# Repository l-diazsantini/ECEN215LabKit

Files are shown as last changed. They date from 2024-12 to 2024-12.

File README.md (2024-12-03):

This is the GitHub repository for Group 30: ECEN 215 Lab Kit from Fall '24, ECEN 404 section 902. This branch contains the firmware code for the final ECEN 215 Lab Kit device. All of the group's reports, presentations, research, meeting notes, etc., can be found in the Documents folder. The PCB and Case folder contains all PCB schematics and case design drawings/markups. All mobile app code can be found in the FlutterFlow branch of this repository.

To operate this device, you must have a physical ECEN 215 Lab Kit and a mobile phone. If using a pre-configured lab kit, the user only needs to press the Enable button through the case to activate the device and connect to it via the mobile application. Please see the FlutterFlow branch for instructions on how to download the application to a mobile device.

If the lab kit is a brand-new PCB, the user will need to connect the Tx, Rx, and GND pins on the PCB to a computer. Once connected, download this code, open it in an Espressif IDF environment, and build and flash the PCB. If done successfully, the Lab Kit will be ready for Bluetooth connection via the mobile application. To operate the lab kit, connect the wires of the corresponding instrument and the device will display the data measured. The wires are given in the order from top row and from left to right:  
<div align="center">
  |  +5v power supply  |  +voltmeter/+oscilloscope  |  ground                    |  +ammeter   |  +ohmmeter |<br>
                                                   |   Wavegen           |  -5v power supply          |  -voltmeter/-oscilloscope  |  -ammeter   |  -ohmmeter  |
</div>
<br>Wires are also color coded in which the wires for +/- power supply are red, +/- voltmeter/oscilloscope are blue, +/- ammeter are orange, +/- ohmmeter are brown, ground is black, and Wavegen is yellow.<br>

The information below provides further insight into how this code enables the onboard ESP32 to connect via Bluetooth.

| Supported Targets | ESP32 | ESP32-C2 | ESP32-C3 | ESP32-C6 | ESP32-H2 | ESP32-S3 |
| ----------------- | ----- | -------- | -------- | -------- | -------- | -------- |

# ESP-IDF Gatt Server Example

This example shows how create a GATT service by adding attributes one by one. However, this method is defined by Bluedroid and is difficult for users to use.

Hence, we also allow users to create a GATT service with an attribute table, which releases the user from adding attributes one by one. And it is recommended for users to use. For more information about this method, please refer to [gatt_server_service_table_demo](../gatt_server_service_table).

This demo creates GATT a service and then starts advertising, waiting to be connected to a GATT client.

To test this demo, we can run the [gatt_client_demo](../gatt_client), which can scan for and connect to this demo automatically. They will start exchanging data once the GATT client has enabled the notification function of the GATT server.

Please, check this [tutorial](tutorial/Gatt_Server_Example_Walkthrough.md) for more information about this example.

## How to Use Example

Before project configuration and build, be sure to set the correct chip target using:

```bash
idf.py set-target <chip_name>
```

### Hardware Required

* A development board with ESP32/ESP32-C3/ESP32-C2/ESP32-H2/ESP-S3 SoC (e.g., ESP32-DevKitC, ESP-WROVER-KIT, etc.)
* A USB cable for Power supply and programming

See [Development Boards](https://www.espressif.com/en/products/devkits) for more information about it.

### Build and Flash

Run `idf.py -p PORT flash monitor` to build, flash and monitor the project.

(To exit the serial monitor, type ``Ctrl-]``.)

See the [Getting Started Guide](https://idf.espressif.com/) for full steps to configure and use ESP-IDF to build projects.

### Settings for UUID128

This example works with UUID16 as default. To change to UUID128, follow this steps:

1. Change the UUID16 to UUID128. You can change the UUID according to your needs.

```c
// Create a new UUID128 (using random values for this example)
uint8_t gatts_service_uuid128_test_X[ESP_UUID_LEN_128] = {0x06, 0x18, 0x7a, 0xec, 0xbe, 0x11, 0x11, 0xea, 0x00, 0x16, 0x02, 0x42, 0x01, 0x13, 0x00, 0x04};
```

By adding this new UUID128, you can remove the `#define` macros with the old UUID16.

2. Add the new UUID128 to the profile.

```c
// Change the size of the UUID from 16 to 128
gl_profile_tab[PROFILE_X_APP_ID].service_id.id.uuid.len = ESP_UUID_LEN_128;
// Copy the new UUID128 to the profile
memcpy(gl_profile_tab[PROFILE_X_APP_ID].service_id.id.uuid.uuid.uuid128, gatts_service_uuid128_test_X, ESP_UUID_LEN_128);
```

3. Remove the following line(s)
```c
gl_profile_tab[PROFILE_X_APP_ID].service_id.id.uuid.uuid.uuid16 = GATTS_SERVICE_UUID_TEST_X;
```

## Example Output

```
I (0) cpu_start: Starting scheduler on APP CPU.
I (512) BTDM_INIT: BT controller compile version [1342a48]
I (522) system_api: Base MAC address is not set
I (522) system_api: read default base MAC address from EFUSE
I (522) phy_init: phy_version 4670,719f9f6,Feb 18 2021,17:07:07
I (922) GATTS_DEMO: REGISTER_APP_EVT, status 0, app_id 0

I (932) GATTS_DEMO: CREATE_SERVICE_EVT, status 0,  service_handle 40

I (942) GATTS_DEMO: REGISTER_APP_EVT, status 0, app_id 1

I (952) GATTS_DEMO: SERVICE_START_EVT, status 0, service_handle 40

I (952) GATTS_DEMO: ADD_CHAR_EVT, status 0,  attr_handle 42, service_handle 40

I (962) GATTS_DEMO: the gatts demo char length = 3

I (962) GATTS_DEMO: prf_char[0] =11

I (972) GATTS_DEMO: prf_char[1] =22

I (972) GATTS_DEMO: prf_char[2] =33

I (982) GATTS_DEMO: CREATE_SERVICE_EVT, status 0,  service_handle 44

I (982) GATTS_DEMO: ADD_DESCR_EVT, status 0, attr_handle 43, service_handle 40

I (992) GATTS_DEMO: SERVICE_START_EVT, status 0, service_handle 44

I (1002) GATTS_DEMO: ADD_CHAR_EVT, status 0,  attr_handle 46, service_handle 44

I (1012) GATTS_DEMO: ADD_DESCR_EVT, status 0, attr_handle 47, service_handle 44

```

## Troubleshooting

For any technical queries, please open an [issue](https://github.com/espressif/esp-idf/issues) on GitHub. We will get back to you soon.

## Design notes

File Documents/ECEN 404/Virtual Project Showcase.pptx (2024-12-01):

## Team 30: ECEN 215 Lab Kit Bi-Weekly Update 5 Members: Luis Diaz-Santini, Yusuf Hossain, Ryan Freed, and Peter Zhang Sponsor: Dr. Lusher TA: Garret Brown

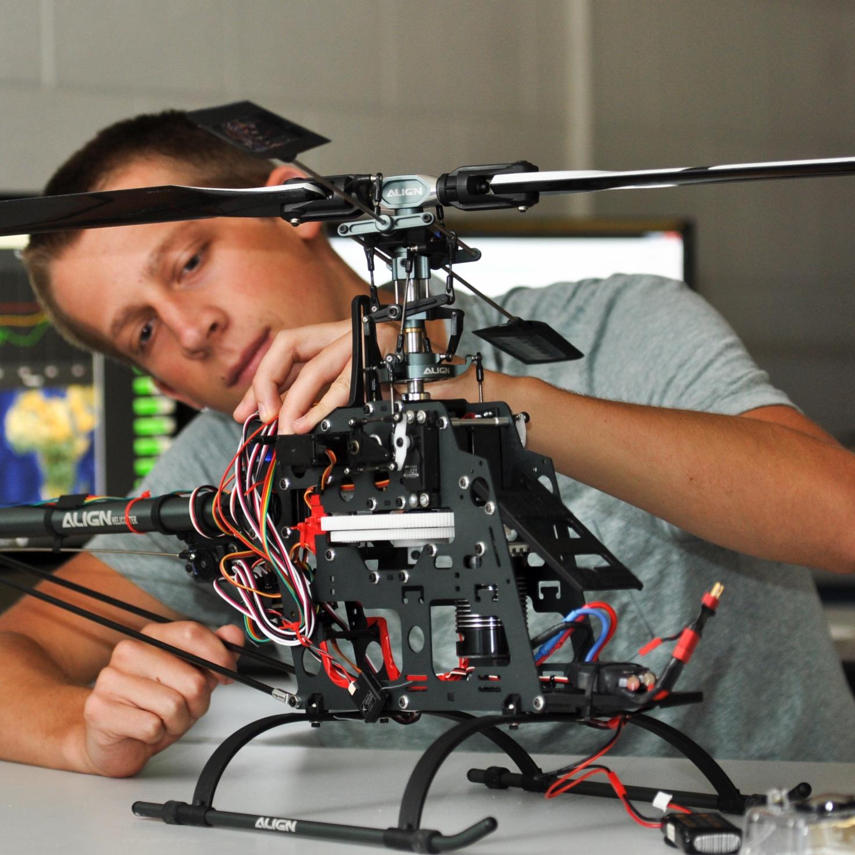
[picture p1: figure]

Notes: Intro should take 30 seconds

## Project Summary

Problem Statement:
- Principles of Electrical Engineering (ECEN 215) teaches the basics of electric circuit analysis and electronics to non-ECEN majors.
- The transition of ECEN 215 to an online format poses a challenge due to its lab component relying on the Analog Discovery 2 (AD2), which is expensive.
Solution Proposal:
- The ECEN 215 Lab Kit offers a solution to the cost, convenience, and over complication issues that are abundant with the AD2. Aiming for a $50 price point, the lab kit offers a more catered simpler approach to each lab while also making it possible to complete at home.
- Will operate as the power supply, signal generator, multimeter, and Oscilloscope.

## Example Lab

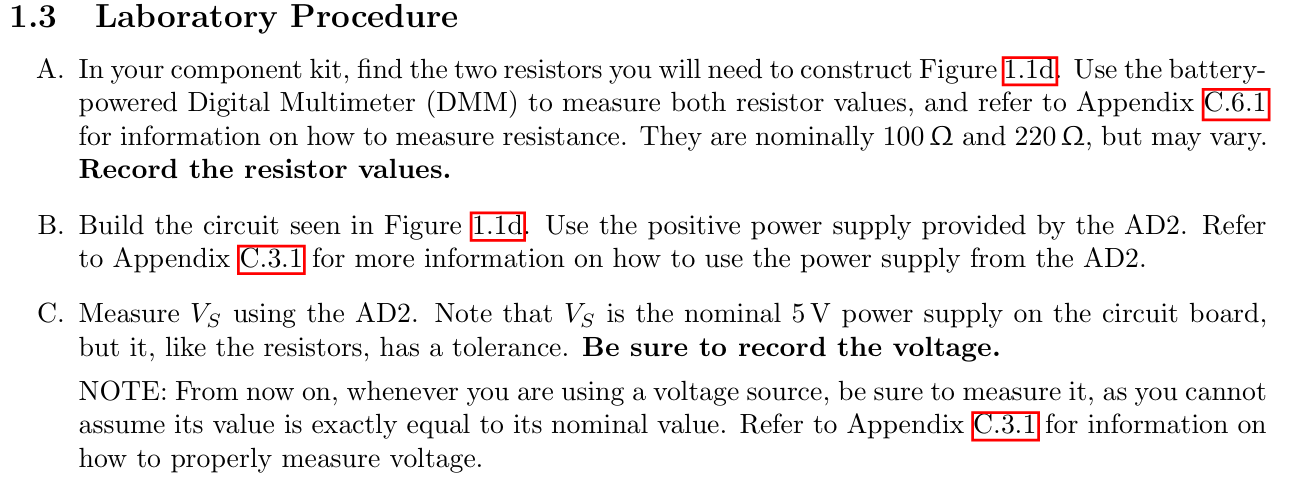
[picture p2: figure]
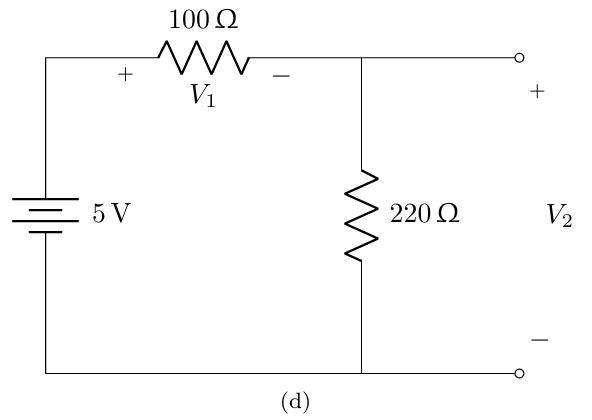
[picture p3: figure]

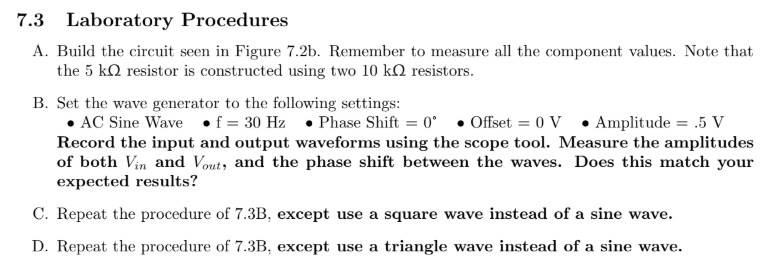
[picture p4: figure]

## Alternatives

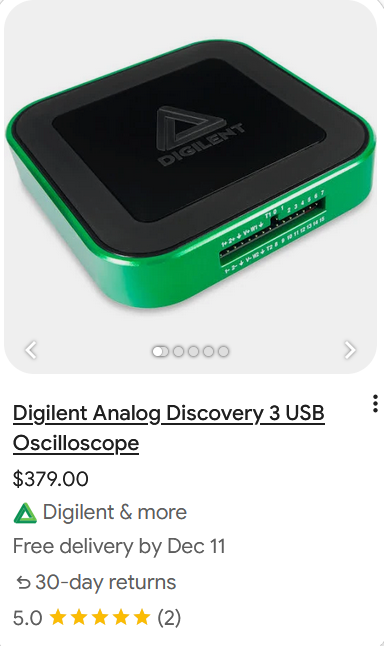
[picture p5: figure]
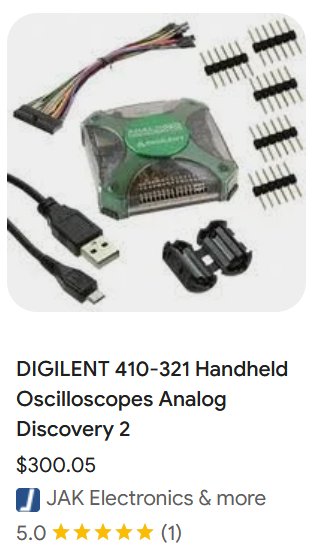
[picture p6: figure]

## Solution Overview

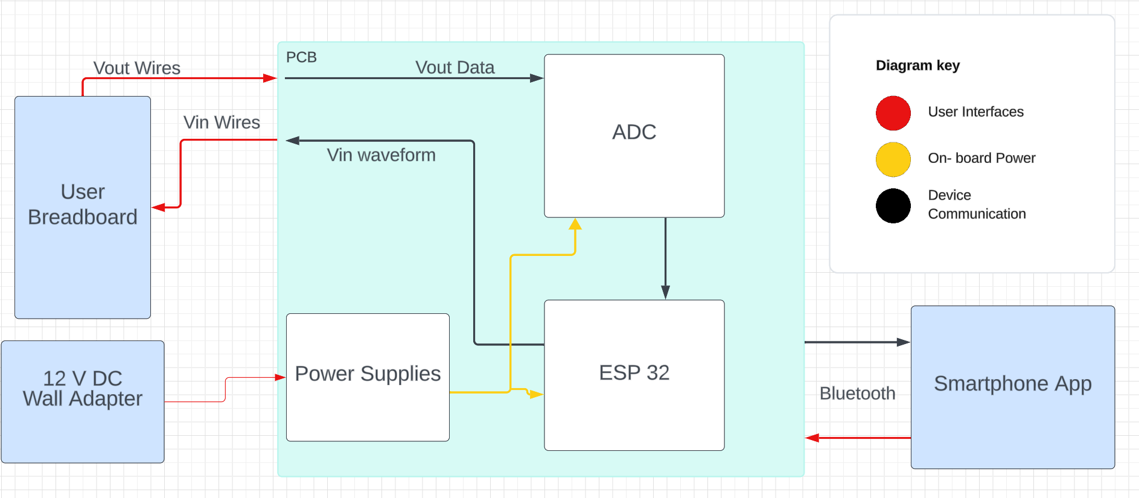
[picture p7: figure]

- Peter: Multimeter and Oscilloscope
- Yusuf: Waveforms and communicating to the microcontroller.
- Luis: Mobile application to interface with device
- Ryan: PCB design and power.

## Oscilloscope and Multimeter Peter Zhang

Accomplishments:
- Design Multimeter (Ammeter, Ohmmeter, Voltmeter)
- Design Oscilloscope
- Read and Modify Data via ESP32
- Transfer Data to App via BLE

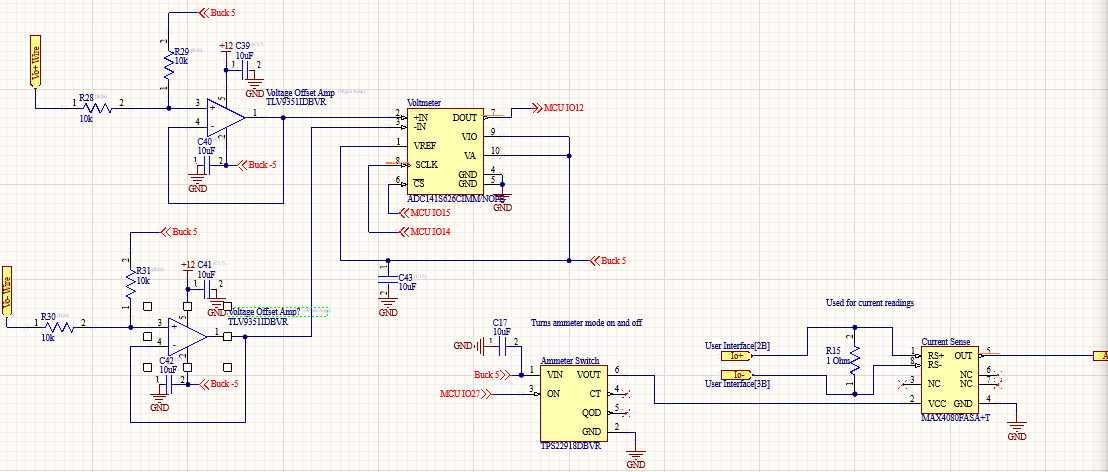
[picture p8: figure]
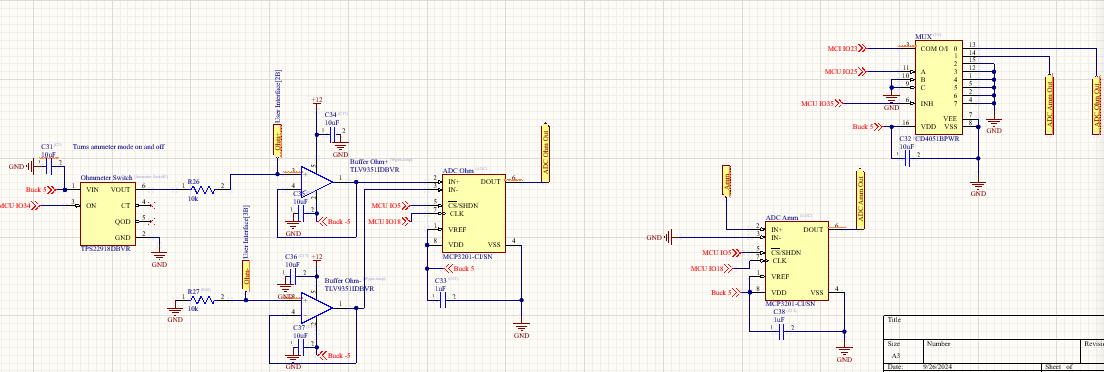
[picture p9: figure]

## Waveform Generator Yusuf Hossain

Validation:

Test | Success Criterion | Results
Wavegen Shapes | Produce Sine, Triangle and square waves
Amplitude | 0.5V, 1V, and 2V
Frequency | 1 Hz, 20 Hz, and 30Hz
Wavegen Noise | Output signal is moderately accurate

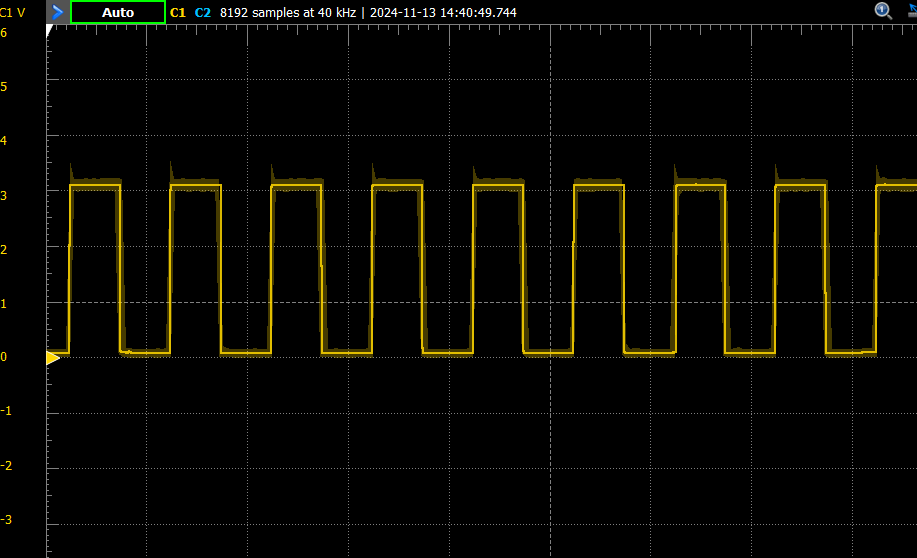
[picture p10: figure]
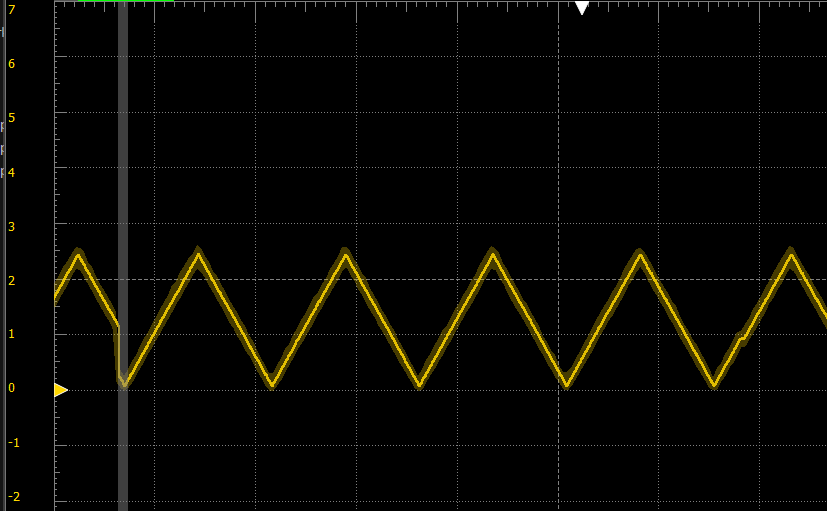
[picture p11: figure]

## Mobile Application

## PCB and Power Ryan Freed

Accomplishments:
- Designed Buck Converters
(5, 3.3, and -5 V)
- Designed Power Supply
switching system (5 and -5 V)
- Designed PCB and case
- Low price and size

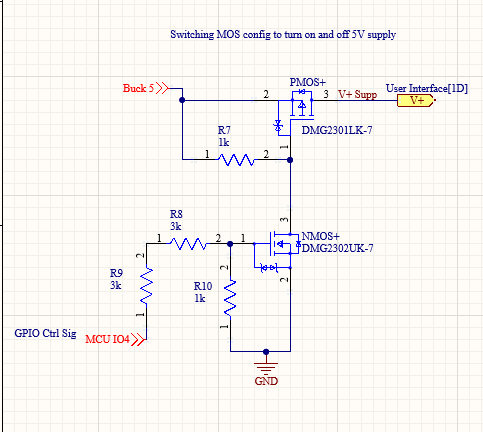
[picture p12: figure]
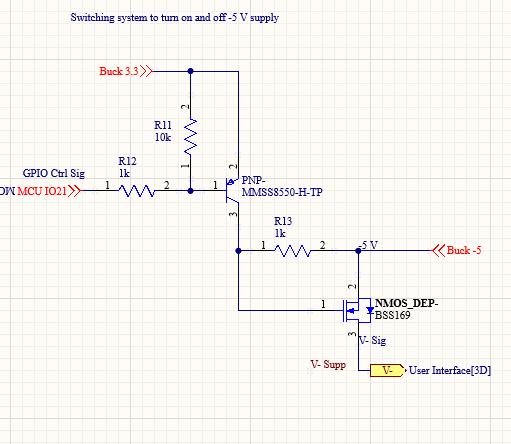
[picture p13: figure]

## Mobile App Validation

- Discovery:
  - Devices are discovered within 4 seconds
- Connection Stability:
  - Verified stable connection to device for at least 30 minutes
- Reconnection:
  - App can disconnect from device and reconnect immediately
- Read/Write Operations:
  - Verified app sending/receiving messages through VSCode terminal and system functionality
- Connection Latency:
  - App constantly connects within 1.5 second
- Command Response Time:
  - Data is sent to the app within 0.25 seconds after requesting
- Device Compatibility:
  - App has been installed and operated on multiple devices with various software anywhere from 2 years of age to 10 years of age
- Interference:
  - In performing this demo the app shows stable connection in an environment with abundant BL traffic

## Multimeter/Oscilloscope Validation

- App-Multimeter Connectivity
  - Microcontroller sends data through bluetooth to the app from terminal and system functionality
- App-Oscilloscope Connectivity:
  - Graphed oscilloscope readings onto app

Voltage
Expected | Actual | Percent Error
5 V | 4.96V | 0.8%
2.5 V | 2.43 | 2.8%
0 V | .024 | ~~~

Resistance
Expected | Actual | Percent Error
10000 | 9814.343 | 1.89%
1000 | 1005.385 | 0.09%
100 | 108.28 | 7.6%

## PCB/Power Validation

Power Systems Results | Expected | Actual
System 1 | 5 V | 4.987
System 2 | 3.3 V | 3.319
System 3 | -5 V | -4.976

Switching System Results | ESP Low | ESP High
Switch 1 | 0.019 mV | 4.93 V
Switch 2 | -4.975 V | -4.973 V

## PCB/Power Validation

Price and Size Analysis:
- Altium Price Analysis: $44.57
- JLC Price Analysis per 500: $3.80
- Wall Adapter: $8.83
- Overall Estimate: $57.20 per board
- Case Size: 156.7x85.6x21.7mm
- Area increase vs. phone: 24%

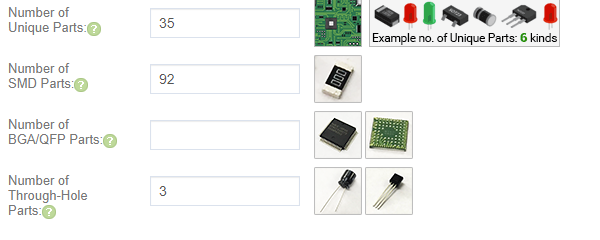
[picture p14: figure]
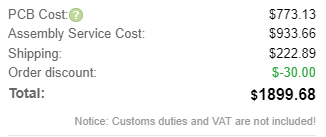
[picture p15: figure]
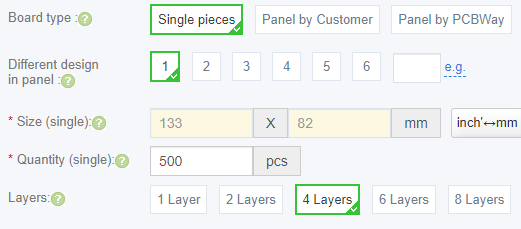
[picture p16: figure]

## ECEN 215 Lab Kit

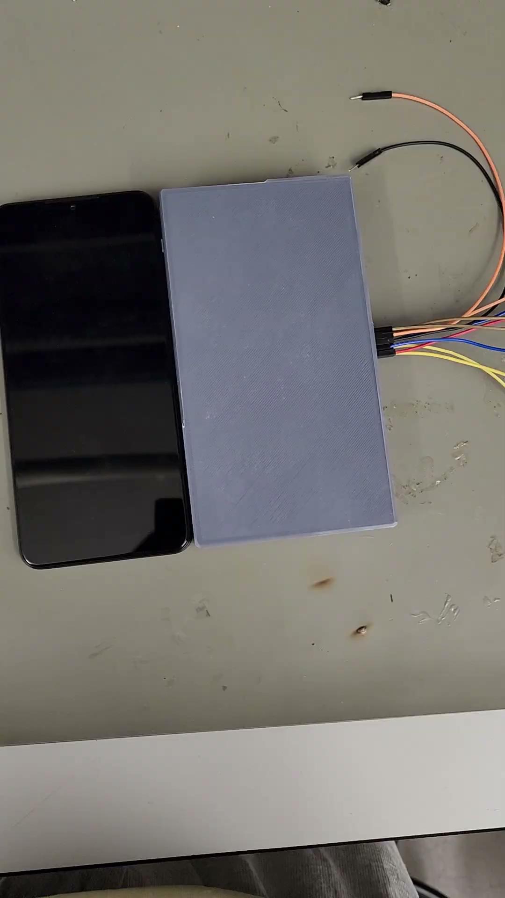
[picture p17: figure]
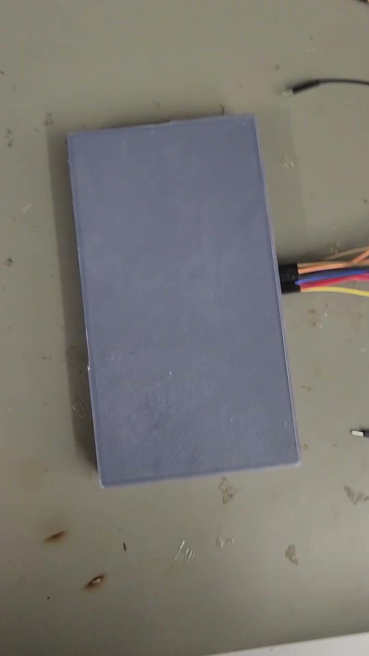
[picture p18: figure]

## Multimeter: Ammeter and Ohmmeter

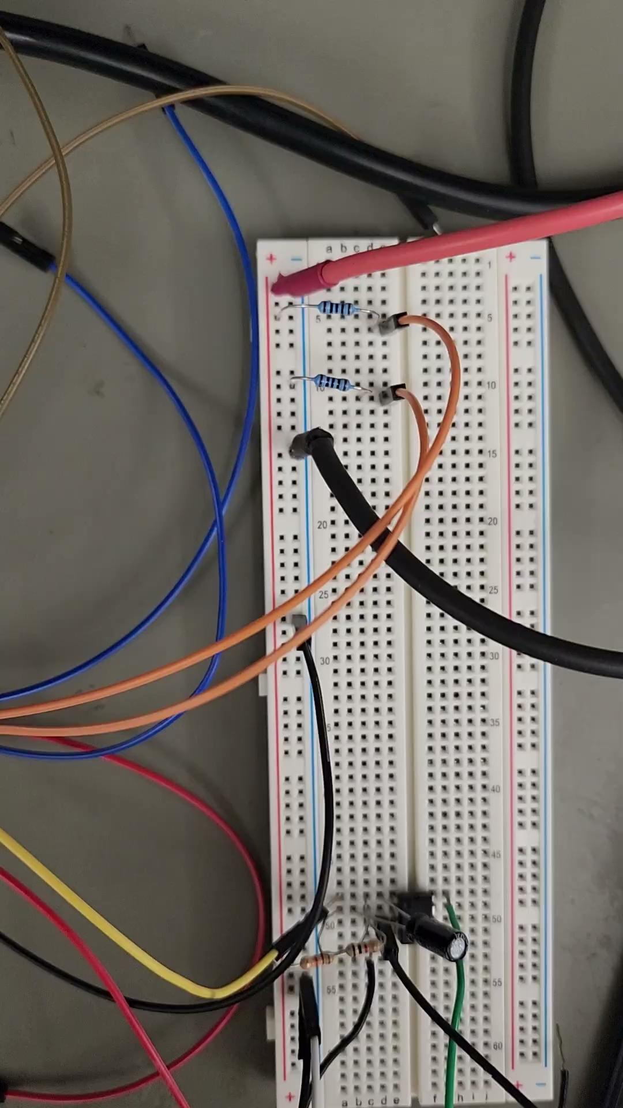
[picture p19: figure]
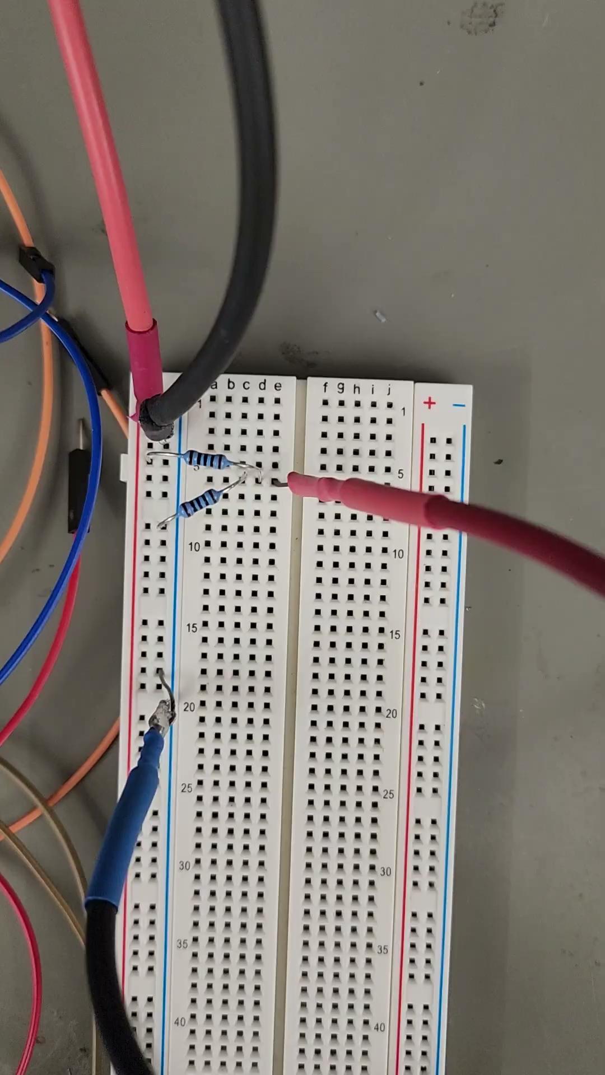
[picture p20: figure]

## Multimeter: Ohmmeter

## Oscilloscope: Sine, Square, and Triangle

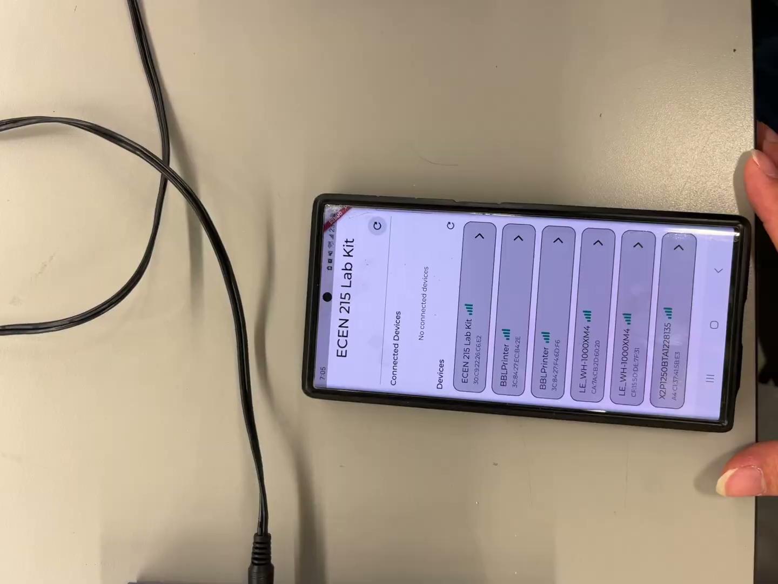
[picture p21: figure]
Sine
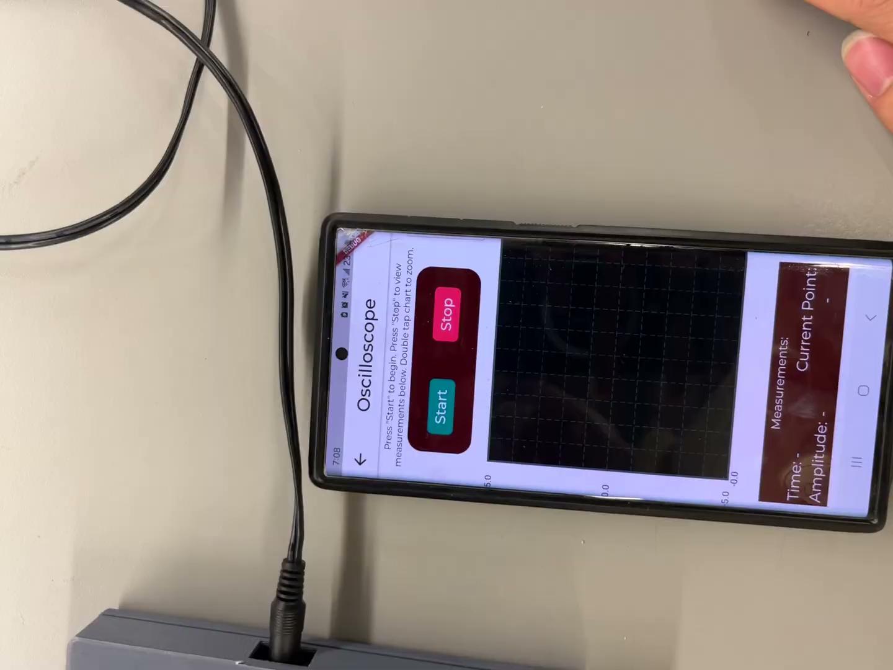
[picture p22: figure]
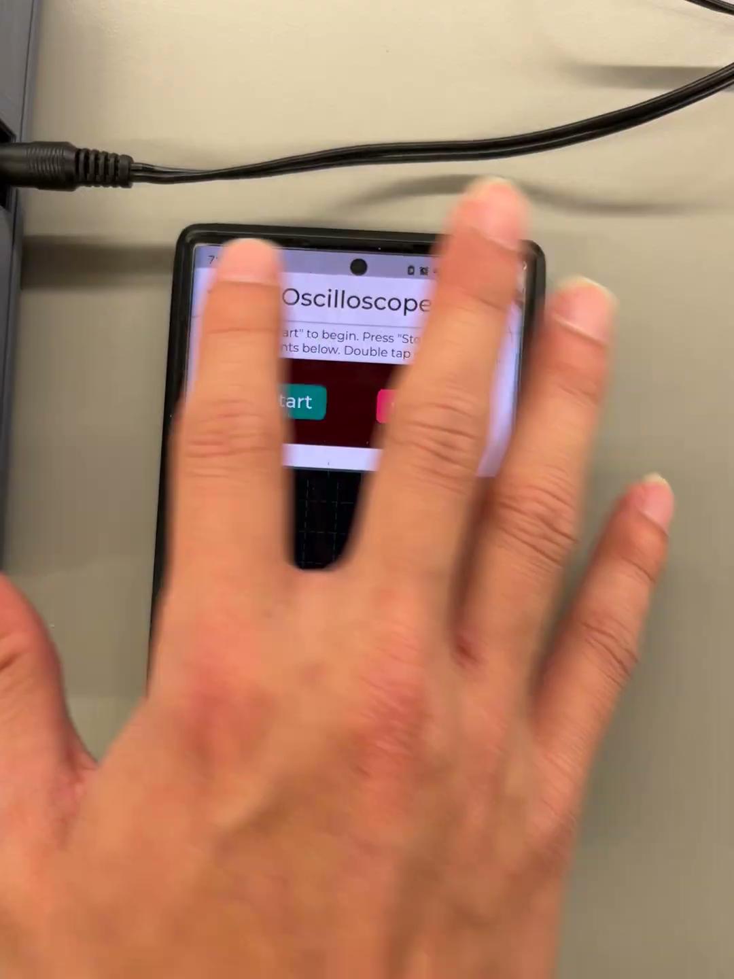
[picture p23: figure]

## Wavegen: Sine, Square, and Triangle

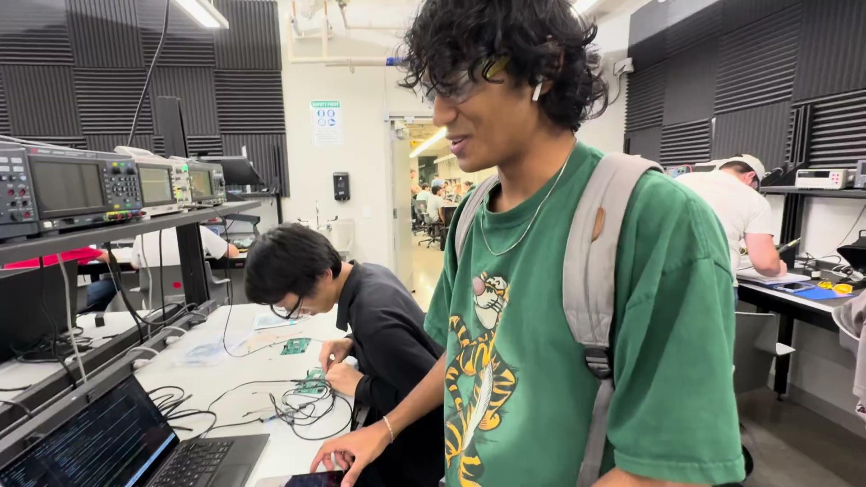
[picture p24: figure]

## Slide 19

Thank you

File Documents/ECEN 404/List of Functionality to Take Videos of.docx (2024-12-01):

Check off what we have recorded:

- Multimeter
  - ~~Voltmeter - measuring 3 different voltages, validate with real multimeter~~
  - Ammeter - measuring 3 different currents, validate with real multimeter
  - ~~Ohmmeter - measuring 3 different resistances, validate with real multimeter~~
- ~~Oscilloscope~~
  - ~~Display constant voltage applied to a system~~
  - ~~Display AC voltages (square, sine, or triangular)~~
  - ~~Show amplitude and time~~
- ~~Waveform Generator (show measurements on an oscilloscope if accurate???)~~
  - ~~Square - all three~~
  - ~~Sine - all three~~
  - ~~Triangular - just the one~~
- Power Supply
  - ~~+5V activation and output~~
  - -5V activation and output

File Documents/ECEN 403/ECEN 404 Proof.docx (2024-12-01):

Peter Zhang


Ryan Freed


Luis Diaz-Santini


Yusuf Hossain


f


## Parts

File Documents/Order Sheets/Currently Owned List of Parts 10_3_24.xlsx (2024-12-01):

Part Name | Disc | Link | Num Parts | I/O (EX: -1) | Date I/O
08055C104JAT4A | 0.1 uF Capacitor | https://www.mouser.com/ProductDetail/KYOCERA-AVX/08055C104JAT4A?qs=xMTsDkQFXIwrNDKsf1C%2F4A%3D%3D | 2
584-AD9833BRMZ | DAC/ADC Special | https://www.mouser.com/ProductDetail/Analog-Devices/AD9833BRMZ?qs=BpaRKvA4VqFt3Bdw9RBKCQ%3D%3D | 1
726-BSS169H6327 | N-Channel Mosfet 2.9 Vgs,th | https://www.mouser.com/ProductDetail/Infineon-Technologies/BSS169-H6327?qs=wsCKvrPXYihFtZGZbPOydw%3D%3D | 2
926-LM2611BMFX/NOPB (https://www.mouser.com/ProductDetail/926-LM2611BMFX-NOPB) | Switching Volt Reg | https://www.mouser.com/ProductDetail/926-LM2611BMFX-NOPB | 1
AC0603FR-0729K4L | 29.4k Resistor | https://www.mouser.com/ProductDetail/YAGEO/AC0603FR-0729K4L?qs=UBLIud9aIG2k8zKS2xVklQ%3D%3D | 7
C0603C331M5HACTU | cer cap | https://www.mouser.com/ProductDetail/KEMET/C0603C331M5HACTU?qs=W0yvOO0ixfErkuKIu%252BxRBQ%3D%3D | 8
C3216X5R1E476M160AC | Cer Cap | https://www.mouser.com/ProductDetail/TDK/C3216X5R1E476M160AC?qs=NRhsANhppD%252BqapdVvBvu4Q%3D%3D | 1
CDBU0130L-HF | Schotty Diode | https://www.mouser.com/ProductDetail/Comchip-Technology/CDBU0130L-HF?qs=2qJf6qQ4IOJ7bRynSa%252B09g%3D%3D | 1
CL21A106KAYNNNF | 10 uF Capacitor | https://www.mouser.com/ProductDetail/Samsung-Electro-Mechanics/CL21A106KAYNNNF?qs=xZ%2FP%252Ba9zWqbNXsT2s0u%252B1w%3D%3D | 1
CRCW060373K2FKEA | Fil Res | https://www.mouser.com/ProductDetail/Vishay-Dale/CRCW060373K2FKEA?qs=wtKLRx7HFiWbNo88VwpoiQ%3D%3D | 8
DMG2301LK-7 | P-Channel MOSFET 0.3 Vgs,th | https://www.mouser.com/ProductDetail/Diodes-Incorporated/DMG2301LK-7?qs=rN85NNvew%2FQ%252B%2FQuwyP8KUg%3D%3D | 1
DMG2302UK-7 | N-Channel MOSFET 0.3 Vgs,th | https://www.mouser.com/ProductDetail/Diodes-Incorporated/DMG2302UK-7?qs=nJRy1mI8RR8oxdwFJAgjOg%3D%3D | 2
LM321LVIDBVR | Op Amp | https://www.mouser.com/ProductDetail/Texas-Instruments/LM321LVIDBVR?qs=qSfuJ%252Bfl%2Fd66sZ569ResAQ%3D%3D | 3
MBR0520-TP | Schotty Diode | https://www.mouser.com/ProductDetail/Micro-Commercial-Components-MCC/MBR0520-TP?qs=Oupk%2FUD005gN%2Fsy5ULAgCw%3D%3D | 3
MBR0580-TP | Schottky Diodes 80V 5.5 A | https://www.mouser.com/ProductDetail/Micro-Commercial-Components-MCC/MBR0580-TP?qs=O1HRStiETCj2wMrWH4Z8DQ%3D%3D | 2
MMSS8550-H-TP | PNP BJT | https://www.mouser.com/ProductDetail/Micro-Commercial-Components-MCC/MMSS8550-H-TP | 2
NR8040T4R7N | 4.7 uH Induct | https://www.mouser.com/ProductDetail/TAIYO-YUDEN/NR8040T4R7N?qs=PzICbMaShUcp7zkwLhhm8A%3D%3D | 1
RK73H1JTTDD1002F | 10K Res | https://www.mouser.com/ProductDetail/KOA-Speer/RK73H1JTTDD1002F?qs=b1MjUb3%252BcaU0rYKbWd%2FWJg%3D%3D | 3
RMCF1210FT1R00 | 1 ohm Res | https://www.mouser.com/ProductDetail/SEI-Stackpole/RMCF1210FT1R00?qs=IPgv5n7u5QY%252BgVPKo7K9fw%3D%3D | 8
RT0603FRE0745K3L | Fil Res | https://www.mouser.com/ProductDetail/YAGEO/RT0603FRE0745K3L?qs=4CyHz7GXqSjZdK2aq1DdCA%3D%3D | 8
SRP1265WA-470M | Pow Induct | https://www.mouser.com/ProductDetail/Bourns/SRP1265A-470M?qs=7z%252BmIopC6%2FJVBbWifq3cvA%3D%3D | 1
SRR1260-150M | Pow Induct | https://www.mouser.com/ProductDetail/Bourns/SRR1260-150M?qs=y9m3SKnhpLPF5BoYDkDwgQ%3D%3D | 2
TPS22918DBVR | Power Switch | https://www.mouser.com/ProductDetail/Texas-Instruments/TPS22918DBVR?qs=f4l5qYp%2Fy%252B5F7w5ZAgmi7A%3D%3D | 1
TPS629203QDRLRQ1 (https://www.mouser.com/ProductDetail/595-TPS629203QDRLRQ1) | Switching voltage regulator 3V to 17V | https://www.mouser.com/ProductDetail/595-TPS629203QDRLRQ1 | 5
CL21A226MAYNNNE | 22 uF Capacitor | https://www.mouser.com/ProductDetail/Samsung-Electro-Mechanics/CL21A226MAYNNNE?qs=xZ%2FP%252Ba9zWqY%2FVvCfXjMhqg%3D%3D | 6
710-694108105102 | Horizontal Wall Wort | https://www.mouser.com/ProductDetail/Wurth-Elektronik/694108105102?qs=a9WhcLg8qCxZ8uWYc7A1TQ%3D%3D | 1
EVQQ1D06M | Button | https://www.mouser.com/ProductDetail/Panasonic/EVQ-Q1D06M?qs=aeOb9a4xWfmdGmKk3ZcvYg%3D%3D | 2
EVP-AKE31A | Button | https://www.mouser.com/ProductDetail/Panasonic/EVP-AKE31A?qs=EU6FO9ffTwe%252BJzX5LvvHqA%3D%3D | 3
PREC003SAAN-RC | Male-Male Vertical header | https://www.digikey.com/en/products/detail/sullins-connector-solutions/PREC003SAAN-RC/2774851?s=N4IgTCBcDaIAoCUCiBhADGgzAZQIK4DkBaBFEAXQF8g | 9
CL10A105KA8NNND | 1 uF Cap | https://www.mouser.com/ProductDetail/Samsung-Electro-Mechanics/CL10A105KA8NNND?qs=xZ%2FP%252Ba9zWqZr4yEmwBAKRg%3D%3D | 7
CR0805-FX-3001ELF | 3k Res | https://www.mouser.com/ProductDetail/Bourns/CR0805-FX-3001ELF?qs=4vGXhLEMbUyE0MonUw6pjA%3D%3D | 5
356-ESP32C6WROOM1N8 (https://www.mouser.com/ProductDetail/356-ESP32C6WROOM1N8) | ESP32-C6-WROOM-1-N8 (https://www.mouser.com/ProductDetail/356-ESP32C6WROOM1N8) | https://www.mouser.com/ProductDetail/356-ESP32C6WROOM1N8

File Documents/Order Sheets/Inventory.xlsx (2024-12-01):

Part name | Desc | Link | Current Inventory | Required Inventory |  | Minimum needed | If neg don't need it | Buck Needs
694108105102 | Power Jack | https://www.mouser.com/ProductDetail/Wurth-Elektronik/694108105102?qs=a9WhcLg8qCxZ8uWYc7A1TQ%3D%3D | 1 | 1 |  | 0
08055C104JAT4A | 0.1 uF 50VDC | https://www.mouser.com/ProductDetail/KYOCERA-AVX/08055C104JAT4A?qs=xMTsDkQFXIwrNDKsf1C%2F4A%3D%3D | 22 | 16 |  | -6 |  | 8 | *
AC0603FR-0729K4L | 29.4k 100mW | https://www.mouser.com/ProductDetail/YAGEO/AC0603FR-0729K4L?qs=UBLIud9aIG2k8zKS2xVklQ%3D%3D | 7 | 1 |  | -6
ADC141S626CIMM/NOPB | ADC 14 bit | https://www.mouser.com/ProductDetail/Texas-Instruments/ADC141S626CIMM-NOPB?qs=7X5t%252BdzoRHCk2zqpP70%252BpA%3D%3D | 1 | 1 |  | 0
BSS169 | NMOS 100V 90mA | https://www.mouser.com/ProductDetail/Infineon-Technologies/BSS169H6327XT?qs=Pidqk4Lw9ynD4CFbvj57WQ%3D%3D | 2 | 1 |  | -1
C0603C331M5HACTU | 333pF 50VDC | https://www.mouser.com/ProductDetail/KEMET/C0603C331M5HACTU?qs=W0yvOO0ixfErkuKIu%252BxRBQ%3D%3D | 8 | 1 |  | -7
C3216X5R1E476M160AC |  | https://www.mouser.com/ProductDetail/TDK/C3216X5R1E476M160AC?qs=NRhsANhppD%252BqapdVvBvu4Q%3D%3D | 1 | 2 | Replaced by MLASE31LBB5476MTNA01 | 1 |  | 2
CD4051BPWR | 8 channel mux | https://www.mouser.com/ProductDetail/Texas-Instruments/CD4051BPWR?qs=dQbkqP7qjabkyiIdB0m30Q%3D%3D |  | 1 |  | 1
CL10A105KA8NNND | 1uF 25VDC | https://www.mouser.com/ProductDetail/Samsung-Electro-Mechanics/CL10A105KA8NNND?qs=xZ%2FP%252Ba9zWqZr4yEmwBAKRg%3D%3D | 7 | 3 |  | -4
CL21A106KAYNNNF | 10uF 25VDC | https://www.mouser.com/ProductDetail/Samsung-Electro-Mechanics/CL21A106KAYNNNF?qs=xZ%2FP%252Ba9zWqbNXsT2s0u%252B1w%3D%3D | 11 | 14 |  | 3 |  | 2 | *
CL21A226MAYNNNE | 22uF 25VDC | https://www.mouser.com/ProductDetail/Samsung-Electro-Mechanics/CL21A226MAYNNNE?qs=xZ%2FP%252Ba9zWqY%2FVvCfXjMhqg%3D%3D | 6 | 2 |  | -4
CR0805-FX-3001ELF | 3k 125mW | https://www.mouser.com/ProductDetail/Bourns/CR0805-FX-3001ELF?qs=4vGXhLEMbUyE0MonUw6pjA%3D%3D | 5 | 2 |  | -3
CRCW060373K2FKEA | 73.2k 100mW | https://www.mouser.com/ProductDetail/Vishay-Dale/CRCW060373K2FKEA?qs=wtKLRx7HFiWbNo88VwpoiQ%3D%3D | 8 | 1 |  | -7
DMG2301LK-7 | PMOS 20VDS | https://www.mouser.com/ProductDetail/Diodes-Incorporated/DMG2301LK-7?qs=rN85NNvew%2FQ%252B%2FQuwyP8KUg%3D%3D | 1 | 1 |  | 0
DMG2302UK-7 | NMOS 20VDS | https://www.mouser.com/ProductDetail/Diodes-Incorporated/DMG2302UK-7?qs=nJRy1mI8RR8oxdwFJAgjOg%3D%3D | 2 | 1 |  | -1
ECS-2520MVLC-041-BN-TR |  | https://www.mouser.com/ProductDetail/ECS/ECS-2520MVLC-041-BN-TR?qs=DPoM0jnrROWVbh6tHYCmfA%3D%3D |  | 1 |  | 1
ESP32-WROOM-32E (4MB) |  |  |  | 1 |  | 1
EVP-AKE31A | Buttons | https://www.mouser.com/ProductDetail/Panasonic/EVP-AKE31A?qs=EU6FO9ffTwe%252BJzX5LvvHqA%3D%3D | 3 | 2 |  | -1
LM2611BMFX | Switch Volt Reg Neg | https://www.mouser.com/ProductDetail/Texas-Instruments/LM2611BMFX-NOPB?qs=X1J7HmVL2ZGO3szAPbzB4g%3D%3D | 1 | 1 |  | 0
MAX4080FASA+T | Current Sense Amp | https://www.mouser.com/ProductDetail/Analog-Devices-Maxim-Integrated/MAX4080FASA%2bT?qs=1eQvB6Dk1vjfAr56%2FBnBlw%3D%3D |  | 1 |  | 1
MBR0580-TP | schottky rectifiers | https://www.mouser.com/ProductDetail/Micro-Commercial-Components-MCC/MBR0580-TP?qs=O1HRStiETCj2wMrWH4Z8DQ%3D%3D | 2 | 1 |  | -1
MCP3201-CI/SN | 12 bit ADC | https://www.mouser.com/ProductDetail/Microchip-Technology/MCP3201-CI-SN?qs=9y3LFqDLL8L6Qsy36gCZ%252Bw%3D%3D |  | 2 |  | 2
MMSS8550-H-TP | BJT PNP 625 mW, 25V | https://www.mouser.com/ProductDetail/Micro-Commercial-Components-MCC/MMSS8550-H-TP | 2 | 1 |  | -1
NR8040T4R7N | Old Button | https://www.mouser.com/ProductDetail/TAIYO-YUDEN/NR8040T4R7N?qs=PzICbMaShUcp7zkwLhhm8A%3D%3D | 7 | 2 |  | -5 |  | 2
OP279GSZ | Output Op Amp rail to rail | https://www.mouser.com/ProductDetail/Analog-Devices/OP279GSZ?qs=WIvQP4zGanjfloKg100C0A%3D%3D |  | 1 |  | 1
PREC003SAAN-RC | Pins | https://www.digikey.com/en/products/detail/sullins-connector-solutions/PREC003SAAN-RC/2774851 | 9 | 1 |  | -8
RK73H1JTTDD1002F | 10k ohm 100mW | https://www.mouser.com/ProductDetail/KOA-Speer/RK73H1JTTDD1002F?qs=b1MjUb3%252BcaU0rYKbWd%2FWJg%3D%3D | 53 | 16 |  | -37
RMCF1210FT1R00 | 1 ohm 500mW | https://www.mouser.com/ProductDetail/SEI-Stackpole/RMCF1210FT1R00?qs=IPgv5n7u5QY%252BgVPKo7K9fw%3D%3D | 8 | 1 |  | -7
RNCP0805FTD1K00 | 1k 250mW | https://www.mouser.com/ProductDetail/SEI-Stackpole/RNCP0805FTD1K00?qs=FESYatJ8odKy9z1hnQn%252Bhg%3D%3D |  | 4 |  | 4
RT0603FRE0745K3L | 45.3K 100mW | https://www.mouser.com/ProductDetail/YAGEO/RT0603FRE0745K3L?qs=4CyHz7GXqSjZdK2aq1DdCA%3D%3D | 8 | 1 |  | -7
SRP1265A-470M | Pow Induct 47uH | https://www.mouser.com/ProductDetail/Bourns/SRP1265A-470M?qs=7z%252BmIopC6%2FJVBbWifq3cvA%3D%3D | 4 | 1 |  | -3 |  | 1
SRR1260-150M | Pw Induct 15uH | https://www.mouser.com/ProductDetail/Bourns/SRR1260-150M?qs=y9m3SKnhpLPF5BoYDkDwgQ%3D%3D | 2 | 1 |  | -1
TLV9351IDBVR | Low power Op Amp | https://www.mouser.com/ProductDetail/Texas-Instruments/TLV9351IDBVR?qs=bAKSY%2FctAC7JwD6JDVCW2g%3D%3D |  | 5 |  | 5
TPS22918DBVR | Power Switch IC | https://www.mouser.com/ProductDetail/Texas-Instruments/TPS22918DBVR?qs=f4l5qYp%2Fy%252B5F7w5ZAgmi7A%3D%3D | 1 | 2 |  | 1
TPS562231DRLR | Switch Volt Reg Pos | https://www.mouser.com/ProductDetail/Texas-Instruments/TPS562231DRLR?qs=l4Gc20tDgJK5KnXgCyg0Bw%3D%3D | 10 | 2 |  | -8
TSM-105-01-T-DH | Wire Header | https://www.mouser.com/ProductDetail/Samtec/TSM-105-01-T-DH?qs=iT52DjcXuds3PBD31HYD6Q%3D%3D |  | 1 |  | 1
MLASE31LBB5476MTNA01 | 47 uF 16VDC | https://www.mouser.com/ProductDetail/TAIYO-YUDEN/MLASE31LBB5476MTNA01?qs=tlsG%2FOw5FFh4KFcjPRamYQ%3D%3D | 10 | 2 | Replaces C3216X5R1E476M160AC | -8

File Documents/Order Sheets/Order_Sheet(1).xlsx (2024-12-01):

356-ESP32C6DKC1N8 | Part Number: | Item Name: | Location to Buy From | Cost per Part | Quantity: | Total Cost: | Item Description:
$4.95 | 584-AD9833BRMZ | ADCs/DAC Specialized | https://www.mouser.com/ProductDetail/Analog-Devices/AD9833BRMZ?qs=BpaRKvA4VqFt3Bdw9RBKCQ%3D%3D | $13.290 | 1 | $13.29 | Wave Gen chip
2024-02-19 | 1965-ESP32-DEVKITC-32UE-ND | ESP32-DEVKITC-32UE | https://www.digikey.com/en/products/detail/espressif-systems/ESP32-DEVKITC-32UE/12091813 | $10.000 | 1 | $10.00 | ESP32 Microcontroller
2024-02-19 | 926-ADC08100CIMTCNPB | ADC 8-bit 100 MSPS | https://www.mouser.com/ProductDetail/Texas-Instruments/ADC08100CIMTC-NOPB?qs=7X5t%252BdzoRHDOkS2%252B9%2FZhUQ%3D%3D | $10.390 | 1 | $10.39 | ADC 8-bit 20-100 Msps
2024-02-28 | ECS-2520SMV-400-FN-TR | ECS standard clock oscillator | https://www.mouser.com/ProductDetail/520-EC2520SMV400FNTR | $2.150 | 2 | $4.30 | Clock signal
2024-02-28 | 584-AD9833BRMZ | ADCs/DAC Specialized | https://www.mouser.com/ProductDetail/Analog-Devices/AD9833BRMZ?qs=BpaRKvA4VqFt3Bdw9RBKCQ%3D%3D | $13.290 | 1 | $13.29 | Bought second one
2024-02-28 | 535-LCQT-MSOP10 | LCQT-MSOP10 | https://www.mouser.com/ProductDetail/535-LCQT-MSOP10 | $3.180 | 2 | $6.36 | To fit all the chips
2024-03-04 | DT-6554/1m | DTECH FTDI USB to TTL Serial Adapter 3.3V Debug Cable 6 Pin Female Socket Header UART IC FT232RL Chip | https://www.amazon.com/Serial-Adapter-Female-FT232RL-Windows/dp/B08BLKCXL4?th=1 | $16.980 | 1 | $16.98 | FTDI USB serial adapter
2024-03-04 | ADC141S626CIMM/NOPB (https://www.mouser.com/ProductDetail/926-AD141S626CIMMNPB) | ADC 12-bit 50-250 KSPS | https://www.mouser.com/ProductDetail/926-AD141S626CIMMNPB | $10.580 | 2 | $21.16 | ADC 14-bit 50-250 KSPS
2024-03-04 | TPS562231DRLR | Switching voltage regulator 4.5V to 17V | https://www.mouser.com/ProductDetail/595-TPS562231DRLR | $0.370 | 5 | $1.85 | Switching Voltage Reuglator
2024-03-04 | TPS629203QDRLRQ1 (https://www.mouser.com/ProductDetail/595-TPS629203QDRLRQ1) | Switching voltage regulator 3V to 17V | https://www.mouser.com/ProductDetail/595-TPS629203QDRLRQ1 | $1.470 | 5 | $7.35 | Voltage Switching Regulator
2024-03-04 | 485-1230 | 1230 | https://www.mouser.com/ProductDetail/485-1230 | $4.950 | 2 | $9.90 | Adafruit Accessories SMT Breakout 13 pack SOT-23/89/223 TO252
2024-03-04 | 926-LM2611BMFX/NOPB (https://www.mouser.com/ProductDetail/926-LM2611BMFX-NOPB) | LM2611BMFX/NOPB | https://www.mouser.com/ProductDetail/926-LM2611BMFX-NOPB | $3.220 | 3 | $9.66 | Switching Voltage Regulators 1.4MHz Cuk Converter 5-SOT-23 -40 to 125
2024-03-04 | 356-ESP32C6WROOM1N8 (https://www.mouser.com/ProductDetail/356-ESP32C6WROOM1N8) | ESP32-C6-WROOM-1-N8 (https://www.mouser.com/ProductDetail/356-ESP32C6WROOM1N8) | https://www.mouser.com/ProductDetail/356-ESP32C6WROOM1N8 | $3.130 | 2 | $6.26 | Multiprotocol Modules ESP32-C6 module, Wi-Fi 6 in 2.4 GHz band, Bluetooth 5, Zigbee 3.0 and Thread. ESP34-WROOM Compatible
2024-03-04 | 356-ESP32C6DKC1N8 | ESP32-C6-DevKitC-1-N8 | https://www.mouser.com/ProductDetail/356-ESP32C6DKC1N8 | $9.000 | 1 | $9.00 | Multiprotocol Development Tools ESP32-C6 Development Board
2024-03-30 |  | Lab Kit PCB | https://www.4pcb.com/ | $66.000 | 2 | $132.00 | PCB
2024-04-01 | 584-AD9833BRMZ | ADCs/DAC Specialized | https://www.mouser.com/ProductDetail/Analog-Devices/AD9833BRMZ?qs=BpaRKvA4VqFt3Bdw9RBKCQ%3D%3D | $13.290 | 2 | $26.58 | Wave Gen chip | *** Add an extra to total order sheet
2024-04-01 | TPS22918DBVR | Power Switch | https://www.mouser.com/ProductDetail/Texas-Instruments/TPS22918DBVR?qs=f4l5qYp%2Fy%252B5F7w5ZAgmi7A%3D%3D | $0.560 | 3 | $1.68 | Power Switch ICs - Power Distribution 5.5-V, 2-A, 52-mO load switch with adj. rise time and adj. output discharge 6-SOT-23 -40 to 105
2024-04-01 | LM321LVIDBVR | Op amp | https://www.mouser.com/ProductDetail/Texas-Instruments/LM321LVIDBVR?qs=qSfuJ%252Bfl%2Fd66sZ569ResAQ%3D%3D | $0.260 | 3 | $0.78 | Operational Amplifiers - Op Amps Single, 5.5-V, 1-MHz, 3-mV offset voltage operational amplifier 5-SOT-23 -40 to 125
2024-04-01 | EVQQ1D06M | Button | https://www.mouser.com/ProductDetail/Panasonic/EVQ-Q1D06M?qs=aeOb9a4xWfmdGmKk3ZcvYg%3D%3D | $1.080 | $4.00 | $4.32 | Tactile Switches Tactile Switch Light Touch, SMD
2024-04-01 | 08055C104JAT4A | 0.1 uF Capacitor | https://www.mouser.com/ProductDetail/KYOCERA-AVX/08055C104JAT4A?qs=xMTsDkQFXIwrNDKsf1C%2F4A%3D%3D | $0.071 | 30 | 2.13 | Multilayer Ceramic Capacitors MLCC - SMD/SMT NEW GLOBAL PN KGM21NR71H104JM 50V 0.1uF X7R 0805 5%
2024-04-01 | CL10A105KA8NNND | 1 uF Capacitor | https://www.mouser.com/ProductDetail/Samsung-Electro-Mechanics/CL10A105KA8NNND?qs=xZ%2FP%252Ba9zWqZr4yEmwBAKRg%3D%3D | $0.019 | 10 | 0.19 | Multilayer Ceramic Capacitors MLCC - SMD/SMT 1uF0.125V X5R 1608 0603
2024-04-01 | CL21A106KAYNNNF | 10 uF Capacitor | https://www.mouser.com/ProductDetail/Samsung-Electro-Mechanics/CL21A106KAYNNNF?qs=xZ%2FP%252Ba9zWqbNXsT2s0u%252B1w%3D%3D | $0.121 | 10 | 1.21 | Multilayer Ceramic Capacitors MLCC - SMD/SMT 10uF+/-10% 25V X5R 2 0805
2024-04-01 | CL21A226MAYNNNE | 22 uF Capacitor | https://www.mouser.com/ProductDetail/Samsung-Electro-Mechanics/CL21A226MAYNNNE?qs=xZ%2FP%252Ba9zWqY%2FVvCfXjMhqg%3D%3D | $0.115 | 10 | 1.15 | Multilayer Ceramic Capacitors MLCC - SMD/SMT 22uF+/-20% 25V X5R 2 0805
2024-04-01 | C3216X5R1E476M160AC | 47 uF Capacitor | https://www.mouser.com/ProductDetail/TDK/C3216X5R1E476M160AC?qs=NRhsANhppD%252BqapdVvBvu4Q%3D%3D | $0.860 | 4 | 3.44 | Multilayer Ceramic Capacitors MLCC - SMD/SMT 1206 25VDC 47uF 20% X5R 1.6mm
2024-04-01 | C0603C331M5HACTU | 330 pF Capacitor | https://www.mouser.com/ProductDetail/KEMET/C0603C331M5HACTU?qs=W0yvOO0ixfErkuKIu%252BxRBQ%3D%3D | $0.021 | 10 | 0.21 | Multilayer Ceramic Capacitors MLCC - SMD/SMT 50V 330pF X8R 0603 20%
2024-04-01 | ECS-2520MVLC-041-BN-TR | Clock Oscillator | https://www.mouser.com/ProductDetail/ECS/ECS-2520MVLC-041-BN-TR?qs=DPoM0jnrROWVbh6tHYCmfA%3D%3D | $1.200 | 2 | 2.4 | Standard Clock Oscillators MultiVolt ECS-2520MVLC,Active,XO (Standard),4.096MHz,Enable/Disable,CMOS,1.8V, 2.5V, 3.3V,+/-50ppm,-40 C 85 C,Surface Mount,4-SMD, No Lead,0.098" L x 0.079" W (2.50mm x 2.00mm),0.035" (0.90mm)
2024-04-01 | MAX4080TASA+T | Current Sense Amplifier | https://www.mouser.com/ProductDetail/Analog-Devices-Maxim-Integrated/MAX4080TASA%2bT?qs=1eQvB6Dk1vggLtAF0LXiqA%3D%3D | $3.610 | 2 | 7.22 | Current Sense Amplifiers 76V, High-Side, Current-Sense Amplifiers with Voltage Output
2024-04-01 | MBR0580-TP | Schottky Diodes 80V 5.5 A | https://www.mouser.com/ProductDetail/Micro-Commercial-Components-MCC/MBR0580-TP?qs=O1HRStiETCj2wMrWH4Z8DQ%3D%3D | $0.210 | 3 | 0.63 | Schottky Diodes & Rectifiers Rectifier 80V 5.5A
2024-04-01 | CDBU0130L-HF | Schottky Diodes 30V 100mA | https://www.mouser.com/ProductDetail/Comchip-Technology/CDBU0130L-HF?qs=2qJf6qQ4IOJ7bRynSa%252B09g%3D%3D | $0.420 | 3 | 1.26 | Schottky Diodes & Rectifiers VR=30V, IO=100mA
2024-04-01 | NR8040T4R7N | 4.7 uH Inductor | https://www.mouser.com/ProductDetail/TAIYO-YUDEN/NR8040T4R7N?qs=PzICbMaShUcp7zkwLhhm8A%3D%3D | $0.470 | 4 | 1.41 | Power Inductors - SMD 4.7 uH
2024-04-01 | SRR1260-150M | 15 uH Inductor | https://www.mouser.com/ProductDetail/Bourns/SRR1260-150M?qs=y9m3SKnhpLPF5BoYDkDwgQ%3D%3D | $0.740 | 3 | 2.22 | Power Inductors - SMD 15 uH
2024-04-01 | SRP1265A-470M | 47 uH Inductor | https://www.mouser.com/ProductDetail/Bourns/SRP1265A-470M?qs=7z%252BmIopC6%2FJVBbWifq3cvA%3D%3D | $1.810 | 3 | 5.43 | Power Inductors - SMD 47 uH
2024-04-01 | ESP32-WROOM-32E (4MB) | ESP32-WROOM-32E (4MB) | https://www.mouser.com/ProductDetail/356-ESP32WRM32E132PH | $2.500 | 2 | 5 | Multiprotocol Modules SMD Module ESP32-WROOM-32E, ESP32-D0WD-V3, 4 MB SPI flash, PCB antenna
2024-04-01 | DMG2302UK-7 | N-Channel MOSFET 0.3 Vgs,th | https://www.mouser.com/ProductDetail/Diodes-Incorporated/DMG2302UK-7?qs=nJRy1mI8RR8oxdwFJAgjOg%3D%3D | $0.280 | 3 | 0.84 | MOSFET MOSFET BVDSS: 8V-24V
2024-04-01 | 726-BSS169H6327 | N-Channel MOSFET 2.9 Vgs,th | https://www.mouser.com/ProductDetail/Infineon-Technologies/BSS169-H6327?qs=wsCKvrPXYihFtZGZbPOydw%3D%3D | $0.450 | 3 | 1.35 | MOSFET N-Ch 100V 90mA SOT-23-3
2024-04-01 | DMG2301LK-7 | P-Channel MOSFET 0.3 Vgs,th | https://www.mouser.com/ProductDetail/Diodes-Incorporated/DMG2301LK-7?qs=rN85NNvew%2FQ%252B%2FQuwyP8KUg%3D%3D | $0.320 | 3 | 0.96 | MOSFET MOSFET BVDSS: 8V-24V
2024-04-01 | MMSS8550-H-TP | PNP BJT | https://www.mouser.com/ProductDetail/Micro-Commercial-Components-MCC/MMSS8550-H-TP | $0.250 | 3 | 0.75 | Bipolar Transistors - BJT 625mW, 25V, 1500mA
2024-04-01 | PREC003SAAN-RC | Male-Male Vertical Header | https://www.digikey.com/en/products/detail/sullins-connector-solutions/PREC003SAAN-RC/2774851?s=N4IgTCBcDaIAoCUCiBhADGgzAZQIK4DkBaBFEAXQF8g | $0.100 | 2 | 0.2 | CONN HEADER VERT 3POS 2.54MM
2024-04-01 | 694108402002 | DC Barrel Power Jack | https://www.mouser.com/ProductDetail/Wurth-Elektronik/694108402002?qs=a9WhcLg8qCzJQpyag5XvEQ%3D%3D | $1.210 | 2 | 2.42 | DC Power Connectors WR-DC PwrJk CtrPnTHT Vertical
2024-04-01 | RMCF1210FT1R00 | 1 Ohm Resistor | https://www.mouser.com/ProductDetail/SEI-Stackpole/RMCF1210FT1R00?qs=IPgv5n7u5QY%252BgVPKo7K9fw%3D%3D | $0.049 | 10 | 0.49 | Thick Film Resistors - SMD 1Ohms 1210 0.5W 1% Std Power AEC-Q200
2024-04-01 | RNCP0805FTD1K00 | 1k Resistor | https://www.mouser.com/ProductDetail/SEI-Stackpole/RNCP0805FTD1K00?qs=FESYatJ8odKy9z1hnQn%252Bhg%3D%3D | $0.023 | 10 | $0.23 | Thin Film Resistors - SMD 1KOhms 0805 0.25W 100ppm 1% Hi Pwr Anti-Sulfur
2024-04-01 | CR0805-FX-3001ELF | 3k Resistor | https://www.mouser.com/ProductDetail/Bourns/CR0805-FX-3001ELF?qs=4vGXhLEMbUyE0MonUw6pjA%3D%3D | $0.018 | 10 | 0.18 | Thick Film Resistors - SMD 3K 1%
2024-04-01 | CRCW08055K00FKTA | 5k Resistor | https://www.mouser.com/ProductDetail/Vishay-Dale/CRCW08055K00FKTA?qs=O7pb%252BE5gJ7THvgJkhh%2F2MQ%3D%3D | $0.240 | 6 | 1.44 | Thick Film Resistors - SMD 1/8watt 5Kohms 1%
2024-04-01 | RK73H1JTTDD1002F | 10k Resistor | https://www.mouser.com/ProductDetail/KOA-Speer/RK73H1JTTDD1002F?qs=b1MjUb3%252BcaU0rYKbWd%2FWJg%3D%3D | $0.013 | 10 | 0.13 | Thick Film Resistors - SMD 1/10watts 10Kohms 1%
2024-04-01 | AC0603FR-0729K4L | 29.4k Resistor | https://www.mouser.com/ProductDetail/YAGEO/AC0603FR-0729K4L?qs=UBLIud9aIG2k8zKS2xVklQ%3D%3D | $0.013 | 10 | 0.13 | Thick Film Resistors - SMD 29.4 k Ohms 100 mW 0 603 1% AEC-Q200 Standard Power Version
2024-04-01 | RT0603FRE0745K3L | 45.3k Resistor | https://www.mouser.com/ProductDetail/YAGEO/RT0603FRE0745K3L?qs=4CyHz7GXqSjZdK2aq1DdCA%3D%3D | $0.018 | 10 | 0.18 | Thin Film Resistors - SMD 1/10W 45.3K ohm 1% 50ppm
2024-04-01 | CRCW060373K2FKEA | 73.2k Resistor | https://www.mouser.com/ProductDetail/Vishay-Dale/CRCW060373K2FKEA?qs=wtKLRx7HFiWbNo88VwpoiQ%3D%3D | $0.019 | 10 | 0.19 | Thick Film Resistors - SMD 1/10watt 73.2Kohms 1%
2024-04-01 | TSM-104-01-T-DH | 6 pin Header, wire housing | https://www.mouser.com/ProductDetail/Samtec/TSM-104-01-T-DH?qs=0lQeLiL1qyaZdbYQ%2FSAlhg%3D%3D | $1.110 | 2 | 2.22 | Headers & Wire Housings .100" Surface Mount Terminal Strip
2024-04-01 | ADC141S626CIMM/NOPB (https://www.mouser.com/ProductDetail/926-AD141S626CIMMNPB) | ADC 12-bit 50-250 KSPS | https://www.mouser.com/ProductDetail/926-AD141S626CIMMNPB | $10.580 | 1 | $10.58 | ADC 14-bit 50-250 KSPS
2024-09-10 | 710-694108105102 | horizontal wall wort | https://www.mouser.com/ProductDetail/Wurth-Elektronik/694108105102?qs=a9WhcLg8qCxZ8uWYc7A1TQ%3D%3D | $1.92 | 2 | $3.84 | Horizontal wall wort adapter
2024-09-10 | EVP-AKE31A | Button | https://www.mouser.com/ProductDetail/Panasonic/EVP-AKE31A?qs=EU6FO9ffTwe%252BJzX5LvvHqA%3D%3D | $0.570 | 5 | $2.85 | Horizontal Buttons
2024-09-10 | JLPCB | PCB Board | https://jlcpcb.com/ |  | 5 | $29.60 | PCB board
 |  |  |  |  | Cost | $397.63
 |  |  |  |  | Shipping | 47.94
 |  |  |  |  | 6
 |  |  |  |  | Total Cost | $445.57

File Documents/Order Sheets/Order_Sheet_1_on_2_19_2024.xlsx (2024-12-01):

Date | Part Number: | Item Name: | Location to Buy From | Cost per Part | Quantity: | Total Cost: | Item Description:
2024-02-19 | 584-AD9833BRMZ | ADCs/DAC Specialized | https://www.mouser.com/ProductDetail/Analog-Devices/AD9833BRMZ?qs=BpaRKvA4VqFt3Bdw9RBKCQ%3D%3D | $13.29 | 1 | $13.29 | Wave Gen chip
2024-02-19 | 1965-ESP32-DEVKITC-32UE-ND | ESP32-DEVKITC-32UE | https://www.digikey.com/en/products/detail/espressif-systems/ESP32-DEVKITC-32UE/12091813 | $10.00 | 1 | $10.00 | ESP32 Microcontroller
2024-02-19 | 926-ADC08100CIMTCNPB | ADC 8-bit 100 MSPS | https://www.mouser.com/ProductDetail/Texas-Instruments/ADC08100CIMTC-NOPB?qs=7X5t%252BdzoRHDOkS2%252B9%2FZhUQ%3D%3D | $10.39 | 1 | $10.39 | ADC 8-bit 20-100 Msps

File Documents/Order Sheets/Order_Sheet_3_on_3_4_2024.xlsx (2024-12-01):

Date | Part Number: | Item Name: | Location to Buy From | Cost per Part | Quantity: | Total Cost: | Item Description:
2024-03-04 | DT-6552 | DTECH FTDI USB to TTL Serial 3.3V Adapter Cable TX RX Signal 3 Pin 0.1 inch Pitch Female Socket FT232RL Chip Windows 11 10 8 7 Linux MAC OS (6ft, Black) | https://www.amazon.com/hz/wishlist/ls/3UGDNII2D2EMQ?ref_=wl_share | $16.88 | 1 | $16.88 | serial booting and debugging bare-metal Raspberry Pi with GDB
2024-03-04
2024-03-04
 |  | Combined: | https://www.mouser.com/ProjectManager/ProjectDetail.aspx?AccessID=a3cc5eec90

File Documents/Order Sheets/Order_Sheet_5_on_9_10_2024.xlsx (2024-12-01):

Date | Part Number: | Item Name: | Location to Buy From | Cost per Part | Quantity: | Total Cost: | Item Description:
2024-09-10 | 710-694108105102 | horizontal wall wort | https://www.mouser.com/ProductDetail/Wurth-Elektronik/694108105102?qs=a9WhcLg8qCxZ8uWYc7A1TQ%3D%3D | $1.92 | 2 | $3.84 | Horizontal wall wort adapter
2024-09-10 | EVP-AKE31A | Button | https://www.mouser.com/ProductDetail/Panasonic/EVP-AKE31A?qs=EU6FO9ffTwe%252BJzX5LvvHqA%3D%3D | $0.570 | 5 | $2.85 | Horizontal Buttons
2024-09-10 | JLPCB | PCB Board | https://jlcpcb.com/ |  | 5 | $29.60 | PCB board
 |  |  |  |  | Total Cost | $36.29
 |  | Shared Mouser Cart | https://www.mouser.com/ProjectManager/ProjectDetail.aspx?AccessID=f0abee7a97
https://www.digikey.com/short/1fh8rdzr
https://www.mouser.com/ProjectManager/ProjectDetail.aspx?AccessID=d75a1b701a

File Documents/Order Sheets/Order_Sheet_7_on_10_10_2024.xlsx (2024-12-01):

Date | Part Number: | Item Name: | Location to Buy From | Cost per Part | Quantity: | Total Cost: | Item Description:
2024-10-10 | PCB Ver3 with sencil | PCB Ver 3 with stencil | JLPCB |  | 5 | $38.91
 |  |  | Make sure stencil dimensions are 200 by 150 mm
 |  |  |  | UPS Express Saver |  | $25.87
 |  |  |  |  | Total Cost | $64.78

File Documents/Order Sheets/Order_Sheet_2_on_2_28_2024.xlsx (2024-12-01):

Date | Part Number: | Item Name: | Location to Buy From | Cost per Part | Quantity: | Total Cost: | Item Description:
2024-02-28 | ECS-2520SMV-400-FN-TR | ECS standard clock oscillator | https://www.mouser.com/ProductDetail/520-EC2520SMV400FNTR | $2.15 | 2 | $4.30 | Clock signal
2024-02-28 | 584-AD9833BRMZ | ADCs/DAC Specialized | https://www.mouser.com/ProductDetail/Analog-Devices/AD9833BRMZ?qs=BpaRKvA4VqFt3Bdw9RBKCQ%3D%3D | $13.29 | 1 | $13.29 | Bought second one
2024-02-28 | 535-LCQT-MSOP10 | LCQT-MSOP10 | https://www.mouser.com/ProductDetail/535-LCQT-MSOP10 | $3.18 | 2 | $6.36 | To fit all the chips
 |  | Combined: | https://www.mouser.com/ProjectManager/ProjectDetail.aspx?AccessID=a3cc5eec90

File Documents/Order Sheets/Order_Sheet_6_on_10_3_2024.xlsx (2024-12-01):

Date | Part Number: | Item Name: | Location to Buy From | Cost per Part | Quantity: | Total Cost: | Item Description:
2024-10-03 | TPS562231DRLR | Switching voltage regulator 4.5V to 17V | https://www.mouser.com/ProductDetail/595-TPS562231DRLR | $0.215 | 10 | $2.15 | Switching Voltage Reuglator
2024-10-03 | MCP3201-CI/P | ADC 12 Bit SPI DIP | https://www.mouser.com/ProductDetail/Microchip-Technology/MCP3201-CI-P?qs=mcPJWgAPNre%2FsJDHtNvcCw%3D%3D | $3.250 | 2 | $6.50
2024-10-03 | CD4051BE | Multiplexer DIP | https://www.mouser.com/ProductDetail/Texas-Instruments/CD4051BE?qs=q2XTDbzbm6DxulBsMcV7tA%3D%3D | $0.800 | 2 | $1.60
2024-10-03 | RK73H1JTTDD1002F | 10k Resistor | https://www.mouser.com/ProductDetail/KOA-Speer/RK73H1JTTDD1002F?qs=b1MjUb3%252BcaU0rYKbWd%2FWJg%3D%3D | $0.013 | 50 | $0.65 | Thick Film Resistors - SMD 1/10watts 10Kohms 1%
2024-10-03 | TL084IN | OP Amps | https://www.mouser.com/ProductDetail/Texas-Instruments/TL084IN?qs=sbcp%2F4gpy0%2FB92t6J09IkQ%3D%3D | $0.84 | 1 | $0.84
2024-10-03 | OPA227PAG4 | OP Amps | https://www.mouser.com/ProductDetail/Texas-Instruments/OPA227PAG4?qs=pJP364FAHqQ%252BYwc%2FpZKseg%3D%3D | $4.71 | 1 | $4.71
2024-10-03 | LM358P | OP Amps | https://www.mouser.com/ProductDetail/Texas-Instruments/LM358P?qs=X1HXWTtiZ0QtOTT8%252BVnsyw%3D%3D | $0.15 | 4 | $0.60
2024-10-03 | ADC141S626CIMM/NOPB (https://www.mouser.com/ProductDetail/926-AD141S626CIMMNPB) | ADC 12-bit 50-250 KSPS | https://www.mouser.com/ProductDetail/926-AD141S626CIMMNPB | $10.580 | 1 | $10.58 | ADC 14-bit 50-250 KSPS
2024-10-03 | 08055C104JAT4A | cap | https://www.mouser.com/ProductDetail/KYOCERA-AVX/08055C104JAT4A?qs=xMTsDkQFXIwrNDKsf1C%2F4A%3D%3D | $0.072 | 20 | $1.44
2024-10-03 | MLASE31LBB5476MTNA01 | Cap | https://www.mouser.com/ProductDetail/TAIYO-YUDEN/MLASE31LBB5476MTNA01?qs=tlsG%2FOw5FFh4KFcjPRamYQ%3D%3D | $0.45 | 10 | $4.51
2024-10-03 | CL21A106KAYNNNF | cap | https://www.mouser.com/ProductDetail/Samsung-Electro-Mechanics/CL21A106KAYNNNF?qs=xZ%2FP%252Ba9zWqbNXsT2s0u%252B1w%3D%3D | $0.12 | 10 | $1.21
2024-10-03 | NR8040T4R7N | pow inductor | https://www.mouser.com/ProductDetail/TAIYO-YUDEN/NR8040T4R7N?qs=PzICbMaShUcp7zkwLhhm8A%3D%3D | $0.47 | 6 | $2.82
2024-10-03 | SRP1265A-470M | pow inductor | https://www.mouser.com/ProductDetail/Bourns/SRP1265A-470M?qs=7z%252BmIopC6%2FJVBbWifq3cvA%3D%3D | $1.90 | 4 | $7.60
 |  |  |  |  | Total Cost | $45.21
 |  | Shared Mouser Cart | https://www.mouser.com/ProjectManager/ProjectDetail.aspx?AccessID=dbfb4965ae

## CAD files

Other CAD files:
PCB and Case/PCB Case 2 piece shell with PCB gap mk1 v1.f3d

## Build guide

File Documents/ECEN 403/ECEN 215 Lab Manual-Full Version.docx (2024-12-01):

ECEN 215 Lab Manual Wei Trinh

In Collaboration With

John Tyler

Samuel Villareal

Mina Rahimian

Nathan Gober

Contents

Acknowledgments iii How To Use This Manual iii Lab Report Guidelines iii Notation Conventions iii

I Lab Assignments 1

1 Ohms Law and Kirchoffs Laws 2 1.1 PreLab Calculations . . . . . . . . . . . . . . . . . . . . . . . . . . . . . . . . . . . . . . . 2 1.2 MultiSim Simulations . . . . . . . . . . . . . . . . . . . . . . . . . . . . . . . . . . . . . . 2 1.3 Laboratory Procedure . . . . . . . . . . . . . . . . . . . . . . . . . . . . . . . . . . . . . . 3 1.4 Additional Lab Measurements . . . . . . . . . . . . . . . . . . . . . . . . . . . . . . . . . . 3

2 Lab # 2: Node Voltages and Equivalent Circuits 5 2.1 PreLab Calculations . . . . . . . . . . . . . . . . . . . . . . . . . . . . . . . . . . . . . . . 5 2.2 MultiSim Simulations . . . . . . . . . . . . . . . . . . . . . . . . . . . . . . . . . . . . . . 6 2.3 Laboratory Procedure . . . . . . . . . . . . . . . . . . . . . . . . . . . . . . . . . . . . . . 6

3 Lab # 3: Introduction to Op Amps 7 3.1 PreLab Calculations . . . . . . . . . . . . . . . . . . . . . . . . . . . . . . . . . . . . . . . 7 3.2 MultiSim Simulations . . . . . . . . . . . . . . . . . . . . . . . . . . . . . . . . . . . . . . 7 3.3 Laboratory Procedures . . . . . . . . . . . . . . . . . . . . . . . . . . . . . . . . . . . . . . 8

4 Lab # 4: First Order RL and RC Transients 9 4.1 PreLab Calculations . . . . . . . . . . . . . . . . . . . . . . . . . . . . . . . . . . . . . . . 9 4.2 MultiSim Simulations . . . . . . . . . . . . . . . . . . . . . . . . . . . . . . . . . . . . . . 9 4.3 Laboratory Procedures . . . . . . . . . . . . . . . . . . . . . . . . . . . . . . . . . . . . . . 10

5 Lab # 5: Introduction to AC Signals 12 5.1 PreLab Calculations . . . . . . . . . . . . . . . . . . . . . . . . . . . . . . . . . . . . . . . 12 5.2 MultiSim Simulations . . . . . . . . . . . . . . . . . . . . . . . . . . . . . . . . . . . . . . 12 5.3 Laboratory Procedure . . . . . . . . . . . . . . . . . . . . . . . . . . . . . . . . . . . . . . 13

6 Lab # 6: Frequency Response 14 6.1 PreLab Calculations . . . . . . . . . . . . . . . . . . . . . . . . . . . . . . . . . . . . . . . 14 6.2 MultiSim Simulations . . . . . . . . . . . . . . . . . . . . . . . . . . . . . . . . . . . . . . 14 6.3 Laboratory Procedure . . . . . . . . . . . . . . . . . . . . . . . . . . . . . . . . . . . . . . 15

7 Lab # 7: Operational Amplifier Integrator and Active Filter 17 7.1 PreLab Calculations . . . . . . . . . . . . . . . . . . . . . . . . . . . . . . . . . . . . . . . 17 7.2 MultiSim Simulations . . . . . . . . . . . . . . . . . . . . . . . . . . . . . . . . . . . . . . 17 7.3 Laboratory Procedures . . . . . . . . . . . . . . . . . . . . . . . . . . . . . . . . . . . . . . 18

8 Lab # 8: Introduction to Logic Gates 19 8.1 PreLab Calculations . . . . . . . . . . . . . . . . . . . . . . . . . . . . . . . . . . . . . . . 19 8.2 MultiSim Simulations . . . . . . . . . . . . . . . . . . . . . . . . . . . . . . . . . . . . . . 19 8.3 Laboratory Procedure . . . . . . . . . . . . . . . . . . . . . . . . . . . . . . . . . . . . . . 20

i

9 Lab # 9: Introduction to Microcontrollers 21 9.1 PreLab Calculations . . . . . . . . . . . . . . . . . . . . . . . . . . . . . . . . . . . . . . . 21 9.2 MultiSim Simulations . . . . . . . . . . . . . . . . . . . . . . . . . . . . . . . . . . . . . . 22 9.3 Laboratory Procedure . . . . . . . . . . . . . . . . . . . . . . . . . . . . . . . . . . . . . . 22

II Reference Materials 27

A Appendix A 28 A.1 Main Window . . . . . . . . . . . . . . . . . . . . . . . . . . . . . . . . . . . . . . . . . . . 28 A.2 Components Toolbar . . . . . . . . . . . . . . . . . . . . . . . . . . . . . . . . . . . . . . . 28 A.3 Measurement Toolbar . . . . . . . . . . . . . . . . . . . . . . . . . . . . . . . . . . . . . . 29 A.4 AC and DC Circuits . . . . . . . . . . . . . . . . . . . . . . . . . . . . . . . . . . . . . . . 30 A.5 Making Measurements . . . . . . . . . . . . . . . . . . . . . . . . . . . . . . . . . . . . . . 33 A.6 Presentation of Results . . . . . . . . . . . . . . . . . . . . . . . . . . . . . . . . . . . . . . 37

B Appendix B: Breadboard Basics 39 B.1 How to use the Breadboard . . . . . . . . . . . . . . . . . . . . . . . . . . . . . . . . . . . 39 B.2 Passive Components . . . . . . . . . . . . . . . . . . . . . . . . . . . . . . . . . . . . . . . 40 B.3 Operational Amplifiers . . . . . . . . . . . . . . . . . . . . . . . . . . . . . . . . . . . . . . 44 B.4 Logic Gates . . . . . . . . . . . . . . . . . . . . . . . . . . . . . . . . . . . . . . . . . . . . 45 B.5 Guidelines for Building Circuits . . . . . . . . . . . . . . . . . . . . . . . . . . . . . . . . . 45

C Appendix C: Waveforms 2015 Basics 47 C.1 Contents of the Analog Discovery 2 . . . . . . . . . . . . . . . . . . . . . . . . . . . . . . . 47 C.2 Main Window . . . . . . . . . . . . . . . . . . . . . . . . . . . . . . . . . . . . . . . . . . . 48 C.3 Power Sources . . . . . . . . . . . . . . . . . . . . . . . . . . . . . . . . . . . . . . . . . . . 49 C.4 Making Measurements . . . . . . . . . . . . . . . . . . . . . . . . . . . . . . . . . . . . . . 51 C.5 Example Circuit Measurements . . . . . . . . . . . . . . . . . . . . . . . . . . . . . . . . . 54 C.6 Digital Mutlimeter . . . . . . . . . . . . . . . . . . . . . . . . . . . . . . . . . . . . . . . . 56 C.7 Presentation of Results . . . . . . . . . . . . . . . . . . . . . . . . . . . . . . . . . . . . . . 58

D Appendix D: Introduction to Microcontrollers 60 D.1 Computers, Processors, and Microcontrollers . . . . . . . . . . . . . . . . . . . . . . . . . 60 D.2 MSP432 LaunchPad - Hardware Overview . . . . . . . . . . . . . . . . . . . . . . . . . . . 61 D.3 Energia - Software Overview . . . . . . . . . . . . . . . . . . . . . . . . . . . . . . . . . . . 62

ii

Acknowledgments

I would like to first and foremost thank all the faculty and students whom have provided their input and their support towards the final product of this lab manual. To Mr. Tyler, who was the author of the original lab manual, for supporting this idea from day 1, and constantly providing insight and feedback on the entire lab manual as a whole. To Dr. Villareal, who provided the novel lab material for both Labs #9 and #10, several of the appendices, and who provided a myriad of interesting ideas to improve the quality of various labs. To Dr. Rahimian, who continually gave valuable insight on how to communicate ideas better to the students, and how to make the content easily digestible to all. To Nathan Gober, who provided a base file and many other smaller sections in this lab manual, from guidelines to conventions. And finally, to all my friends and family who consistently provided feedback from a third person perspective, and supported me through this endeavor.

How To Use This Manual

This manual is split into two parts: the laboratory assignments and the reference materials. A lab assignment contains three parts: a pre-lab assignment, a simulation exercise, and an experimental pro cedure. Each part of a lab assignment will help you complete the next part, so it is best if you perform them in order.

In general, the pre-lab assignment will produce an analytical solution for the lab assignment. The simulation will rapidly generate many data points, which will later be compared to the measured results, that should confirm your understanding of the analytical solution. The lab procedure will require you to collect data and present it. The required data collection will be shown in bold text. It should, to within a reasonable degree of error, match the predictions of the previous two parts.

In the reference section, you will find guides and datasheets describing how to use the laboratory equipment. These documents are provided to equip you to complete the assignments easily. You may wish to read through the reference section before the first lab to familiarize yourself with it and make later references faster. However, any time the lab manual references a certain appendix, figure, or table, you may click on the associated number, and it will bring you to the page with the relevant information. ie: Clicking on the A in ”Appendix A” will bring you to the start of the associated appendix.

Lab Report Guidelines

Mark all materials that you turn in with your name (printed legibly) and section.

Pre-lab calculations, analyses, and simulations are individual work and are due at the start of the lab period for that lab. Keep a copy of your results for reference during the lab.

Simulation printouts are required to document your simulations.

Lab reports are due at the time specified by your lab instructor. Due dates are typically one week after the date of the lab period.

Use a professional, technical writing style in your reports. Support all claims with observations and data.

Notation Conventions

In general, this manual will adhere to widely accepted conventions for naming quantities and drawing circuit diagrams. You are encouraged to follow these conventions in your own work. If a circuit diagram deviates from these conventions, follow its conventions where they conflict with these.

Wherever possible, quantities with identical units are given the same letter, and are distinguished by a subscript (e.g. R1, R2). When only one such quantity is present, it is generally given without a subscript. In general,

iii

– V denotes a voltage,

– I denotes a current,

– R denotes a resistance,

– C denotes a capacitance, and

– L denotes an inductance.

Time-constant quantities are notated with capital letters (e.g. R, C).

Time-variant quantities are notated with lowercase letters (e.g. i, v). Where significant, they may also be notated as functions of time, like i(t).

The voltage across a component and the current through it will share a subscript with the com ponent’s name (that is, V1 is the voltage across C1, and i1(t) is the current through it). If the component’s name does not have a subscript, the name is used instead (thus, VS is the voltage across source S).

Current is assumed to flow from high voltages to low voltages (sometimes known as positive current flow).

Time-constant voltages are assumed to be greater than zero.

The following phyiscal constants are also used in this manual:

π ≈ 3.1416 is the ratio of a circle’s circumference to its diameter.

j =√−1 is the imaginary unit.

e ≈ 2.7183 is the base of the natural logarithm.

iv

Part I

Lab Assignments 1

1 Ohms Law and Kirchoffs Laws

1.1 PreLab Calculations. Due at the beginning of lab.

Do not use MultiSim for this part. Read through the entire lab before the start of the lab period. A. Read through the entire lab before the start of the lab period.

B. By hand, using Kirchoff’s and Ohm’s Laws, calculate all indicated quantities in the circuits of Figures 1.1a- 1.1d.

1.2 MultiSim Simulations. Due at the beginning of lab.

Refer to Appendix C for information on how use MultiSim and how to submit your results.

A. Use MultiSim to simulate each of the circuits in Figures 1.1a- 1.1d. A separate meter should be used for each simulated measurement.

B. Print out your schematics showing all the meter’s readings.

C. Tabulate your results, comparing theoretical predictions from Section 1.1. Your tabulated results should numerically demonstrate the validity of Ohm’s Law, KVL, KCL, and the voltage divider.

D. Write a sentence for each figure describing how each demonstrates a specific circuit principle. Refer to Ohm’s Law for Figure 1.1a, KCL for Figure 1.1b, KVL for Figure 1.1c, and voltage dividers for Figure 1.1d.

I

5 kΩ

6 V

+

VR

IS

2 kΩ

10 V

4 kΩ

3 kΩ

−

(a)

2 kΩ

⁺ −

I1

100 Ω

I3

(b)

I2

5 V

V1

3 kΩ

+

V2

⁺ − V1

5 V

+

220 Ω

V2

−

V3

− +

1.5 kΩ

(c)

−

(d)

Figure 1.1: Lab #1 Figures

2

1.3 Laboratory Procedure

A. In your component kit, find the two resistors you will need to construct Figure 1.1d. Use the battery powered Digital Multimeter (DMM) to measure both resistor values, and refer to Appendix C.6.1 for information on how to measure resistance. They are nominally 100 Ω and 220 Ω, but may vary. Record the resistor values.

B. Build the circuit seen in Figure 1.1d. Use the positive power supply provided by the AD2. Refer to Appendix C.3.1 for more information on how to use the power supply from the AD2.

C. Measure VS using the AD2. Note that VS is the nominal 5 V power supply on the circuit board, but it, like the resistors, has a tolerance. Be sure to record the voltage.

NOTE: From now on, whenever you are using a voltage source, be sure to measure it, as you cannot assume its value is exactly equal to its nominal value. Refer to Appendix C.3.1 for information on how to properly measure voltage.

D. Use your measured values of R1, R2, and VS to calculate V1 and V2 as you did in the pre-lab assignment. Record the calculated values of V1 and V2.

E. Measure V1 and V2 using the AD2. Record the measured values of V1 and V2.

F. Compare your calculated voltage values from 1.3D with your measured values from 1.3E. Calculate a percent difference for both V1 and V2.

1.4 Additional Lab Measurements

1.4.1 Photoresistor Measurements

A. What is the measured resistance of the photoresistor when exposed to ambient light? Cover the surface of the photoresistor with cardstock at about .5 inches above the surface. What is the resistance now? What about when you shine a flashlight onto the surface? Record these results in Table 1.

Table 1: Resistance of the Photoresistor

Light Level | Resistance (Ω)
Covered with Cardstock (Dark)
Ambient Light (Neutral)
Flashlight (High)

B. Using the results from Table 1, Give a one to two sentence statement on what happens to the resistance as the light level changes.

C. Modify the circuit in Figure 1.1d by replacing R1 with a 10 kΩ resistor, and replace R2 with the photoresistor. Repeat the procedure from 1.4.1A, but measure the voltage across the photoresistor instead. Record these results in Table 2.

Table 2: Voltage across the Photoresistor

Light Level | Voltage (V)
Covered with Cardstock (Dark)
Ambient Light (Neutral)
Flashlight (High)

D. Again using the results from Table 2, give a one to two sentence statement on what happens to the voltage as the light level changes.

3

1.4.2 Thermistor Measurements

A. What is the measured resistance of the thermistor when exposed to room temperature? Rub the thermistor between your palms to generate some heat, and measure the resistance. Record your results in Table 3.

Table 3: Resistance of the Thermistor

Temperature | Resistance (Ω)
Ambient Temperature (Neutral)
Rubbed Between Palms (Warm)

B. Using the results from Table 3, give a one or two sentence statement on what happens to the resistance as the temperature changes.

C. Modify the circuit in Figure 1.1d by replacing R1 with a 10 kΩ resistor, and replace R2 with the thermistor. Repeat the procedure from 1.4.2A, but measure the voltage across the thermistor instead. Record your results in Table 4.

Table 4: Voltage across the Thermistor

Temperature | Voltage (V)
Ambient Temperature (Neutral)
Rubbed Between Palms (Warm)

D. Again using your results from Table 4, give a one to two sentence statement on what happens to the voltage as the temperature changes.

E. This circuit, containing either of the variable resistors, could be included as the first stage in the design of a control instrument. Write a brief (two or three sentence) description of a practical device which would make use of such a circuit.

4

2 Lab # 2: Node Voltages and Equivalent Circuits

Refer to the circuit seen in Figure 2.1. Resistor values have been selected from available components. Nominal values should be used for calculations and simulations, but as soon as measured values are avail able, they should be used to improve comparisons among calculations, simulations and measurements.

Nominal Measured

R1 = 47 Ω R1 =

R2 = 47 Ω R2 =

R3 = 100 Ω R3 =

R4 = 220 Ω R4 =

RL = 100 Ω RL =

VS = 5 V VS =

S Z

VS

R1

R2

R3

R4

X

+ IL VL

–

Y

RL

Figure 2.1: Lab #2 Figure

2.1 PreLab Calculations. Due at the beginning of lab.

Do not use MultiSim for this part. Read through the entire lab before the start of the lab period. A. Determine IL by the node voltage technique. Choose the ground node wisely.

B. Determine the Thevenin equivalent circuit at nodes x and y. (Remember to disconnect RL first.) Use your results to form a Thevenin equivalent network at nodes x and y. What is the Thevenin voltage and resistance?

C. Reconnect RL at nodes x and y, and use the equivalent network to determine IL. Compare your results with the node voltage method.

D. Now consider RL to be a variable resistor. What value of RL would be required to achieve the maximum power transfer from the active network at x and y to the load resistor RL?

5

2.2 MultiSim Simulations. Due at the beginning of lab.

A. Simulate the original circuit using the given values of RL. Measure IL with an ammeter. Remember, ammeters are connected in series with the current to be measured.

B. Define node z to be ground. Using a voltmeter, measure the node voltages at nodes s, x, and y. Tabulate your results. Use the measured node voltages at x and y to calculate IL.

C. Now delete RL. Measure VOC and ISC at nodes x and y (with RL removed. Use these measurements to design a Norton equivalent network. Build your Norton equivalent network in MultiSim, re attach RL, and measure IL.

D. Restore the original circuit. Prepare a table of VL, IL, and PL (the load resistor power). Demon strate that PL is maximized when RL = RT h. Include at least three values of RL less than RT h, one value equal to RT h, and at least three values of RL greater than RT h.

2.3 Laboratory Procedure

A. Locate all required resistors and measure their resistances with the DMM. Build the original circuit on circuit board using the nominal 5 V power supply for VS. Measure IL with the DMM, and record the value. Remember that ammeters are connected in series with the current to be measured, with positive current flow into the positive terminal of the meter.

B. Measure VL = Vxy using the AD2. Calculate the product IL × RL, where IL is the measured current from the previous circuit. Record both the measured and calculated values, and compare them to each other.

C. Now remove RL and measure VOC and ISC with the necessary tools. Record the values of VOC and ISC .

D. Calculate the Thevenin equivalent circuit at nodes x and y with the measured values of all the components. Draw the Thevnin equivalent circuit, and use it to calculate IL.

E. Simulate the circuit from Figure 2.1 in Multisim using the measured component values. Measure IL using an ammeter. Record IL.

F. Compare your calculated, measured, and simulated load currents IL. What is the percentage difference between the calculated, simulated, and measured values?

6

3 Lab # 3: Introduction to Op Amps

3.1 PreLab Calculations. Due at the beginning of lab.

Do not use MultiSim for this part. Read through the entire lab before the start of the lab period. A. Review the basics of the ideal op amp model.

B. Apply the ideal op amp model to the schematic of the inverting amplifier shown in Figure 3.1. Write the equation relating output voltage to input voltage for this circuit. Use this equation to calculate the output voltage when:

Vin = .5 V R1 = 1 kΩ R2 = 5 kΩ

R2

I2

15 V

R1

Vin

−

Vout

I1

+

-15 V

Figure 3.1: Lab # 3 Inverting Amplifier

3.2 MultiSim Simulations. Due at the beginning of lab.

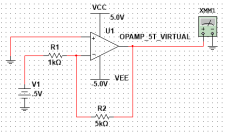
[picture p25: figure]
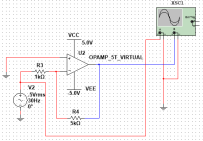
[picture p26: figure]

(a) Lab # 3 DC Circuit (b) Lab # 3 AC Circuit

A. DC Operation. Simulate the circuit shown in Figure 3.2a. Nominal values of R1 and R2 are given in Section 3.1. Use the five terminal virtual op amp as described in Appendix A.4.3, and use the VCC and VEE power sources as your voltage rails. What is the value of Vout? Be careful of the signs of the voltage inputs.

7

B. AC Operation. Simulate the circuit shown in Figure 3.2b. The AC source has a .5 V magnitude at 30 Hz. Measure the amplitudes of both Vin and Vout.

C. AC Operation. Measure the time shift ∆t using cursors. Remember that the time shift is the difference in time between consecutive peaks of two different waves. Refer to Appendix C.4.3 for further details on how to use cursors. Using this time shift, calculate the phase shift ∆φ using the equation below.

∆φ = 360 × ∆t × f

3.3 Laboratory Procedures

A. Collect all the resistors you will need to construct the circuit of Figure 3.2a and Figure 3.2b. For R2, note that you should use 10 kΩ resistors in parallel, which will make an equivalent resistor of 5 kΩ. See Appendix B.2.1 for further details on how to properly wire parallel components. Measure and record all resistor values with the DMM.

B. Build the DC circuit in Figure 3.2a. The input voltage should still be a nominal .5 V DC source provided by the AD2. Refer to Appendix C.3.2 for information on how to generate a DC signal. Pay close attention to power supply connections, and ensure that the +5 V and -5 V sources are in the correct locations.

C. Use the AD2 to measure Vin and Vout. Compare these measurements with Section 3.2. Refer to Appendix C.4 for information on what are the appropriate tools to use.

D. What is the scaling factor for the DC measurements? Report this value and state whether or not it matches what you expect, and why or why not.

E. Now construct the AC circuit seen in Figure 3.2b. Note that this circuit is extremely similar to the DC circuit, but you only need to switch the signal from a DC one to an AC signal. Save the wave forms from the AD2, and present them in your lab report. Refer to Appendix C.7.2 for information on how to submit graphs.

F. Using the cursors on the oscilloscope, measure the amplitude of Vin and Vout. Using these results, what is the scaling factor for the AC measurements? Does this match what you expect?

G. Using the cursors on the oscilloscope, measure the time shift ∆t, and use the same procedure as 3.2C to calculate the phase shift ∆φ.

8

4 Lab # 4: First Order RC and RL Transients 4.1 PreLab Calculations. Due at the beginning of lab. A. For the circuit in Figure 4.1:

Use KVL and the linear models to set up the differential equation for i(t). Solve the differential equation for i(t).

Use this result to calculate vc(t), the voltage across the capacitor for t > 0. t > 0

+

C

R

+

VC

−

i(t) VR −

Figure 4.1: RC Circuit

B. For the circuit in Figure 4.2, given i(0) = I:

Use KVL and the linear models to set up the differential equation for i(t). Solve the differential equation for i(t).

Use this result to calculate vR(t), the voltage across the resistor for t > 0. t > 0

+

L

R

+

VL −

i(t) VR −

Figure 4.2: RL Circuit

4.2 MultiSim Simulations. Due at the beginning of lab.

A. Simulate the circuit in Figure 4.3. Record three to four cycles of both the input and output. Refer to Appendix A.4.5 for information on how to change wire colors, and Appendix A.6 for information on how to present the results. The function generator should have the following settings: • Square Wave • f = 20 Hz • Duty Cycle = 50 % • Offset = 1 V • Amplitude = 1 V

B. Repeat 4.2A, but change the capacitor to a nominal 10 F one.

C. Repeat 4.2A, but change the capacitor to a nominal 100 F one.

D. Calculate τ = RC for all three capacitor values. Use these values to explain the differences among the three output values.

9

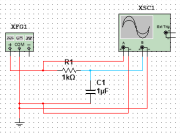
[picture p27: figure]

Figure 4.3: Lab #4 RC Simulation

E. Simulate the circuit in Figure 4.4. Record three to four cycles of both the input and output.

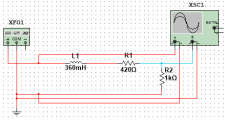
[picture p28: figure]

Figure 4.4: Lab #4 RL Simulation

F. Use the MultiSim scope cursors to measure τ. See Appendix A.5.4 for more details on how to use cursors. When measuring τ, there are two equations that must be considered:

Vcharge(t) = Vmax(1 − e^−t

τ ) (1)

When t = τ for Equation 1, we get that V (τ) = .63Vmax. This means that the time constant, τ, is the time elapsed after 63% of Vmax has been reached from 0%.

Vdischarge(t) = Vmaxe^−t

τ (2)

Conversely, when t = τ for the Equation 2, we get that V (τ) = .37Vmax. This means that the time constant, τ, is the time elapsed after 37% of Vmax is reached. Examples of these measurements are seen in Figure 4.5.

4.3 Laboratory Procedures

4.3.1 RC Circuit

A. Construct Figure 4.3 on the breadboard. Use the wavegen tool from the AD2 as the function generator, and use the same settings as used in Section 4.2:

• Square Wave • f = 20 Hz • Duty Cycle = 50 % • Offset = 1 V • Amplitude = 1 V

Refer to Appendix C.3.2 for details on how to use the wavegen tool. Measure all component values that you will be using in the lab.

10

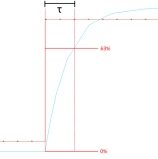
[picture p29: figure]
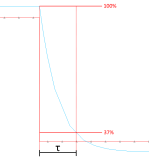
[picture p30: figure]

(a) Measuring τ through Charging (b) Measuring τ through Discharging

Figure 4.5: Measuring τ Examples

B. Using the scope tool from the AD2, present the input and output waveforms using the scope tool. Refer to Appendix C.4.3 for further details on how to use the scope tool.

C. Repeat 4.3.1B for a 10 F capacitor. Remember to record the input and output waveforms. D. Repeat 4.3.1B for a 100 F capacitor. Remember to record the input and output waveforms. E. Calculate τ using measured component values. Report these τ values.

F. Using the τ values from 4.3.1E, explain the differences in the plots from 4.3.1B , 4.3.1C, and 4.3.1D.

4.3.2 RL Circuit

A. Measure both the inductance and the internal resistance of the inductors, and the resistance of the resistor. Record these values in your lab report.

B. Construct Figure 4.4 on the breadboard. Keep in mind two things when constructing the circuit:

Use the three inductors in series to recreate a 360 mH inductor.

The 420 Ω resistor is the sum of the internal resistances of the inductors; NOT an external resistor.

, Use the wavegen tool from the AD2 as the function generator, and use the same settings as used in Section 4.2:

• Square Wave • f = 20 Hz • Duty Cycle = 50 % • Offset = 1 V • Amplitude = 1 V C. Using the scope tool from the AD2, present the input and output waveforms. D. Using the cursors from the scope tool, measure τ using the same method as 4.2F. E. Calculate τ using Equation 3. Record this value, and compare it to the simulated and

calculated values of τ.

τ =L

R + RL(3) 11

5 Lab # 5: Introduction to AC Signals

5.1 PreLab Calculations. Due at the beginning of lab.

A. Given the following equation for a general AC waveform, label V , ω, and φ. A = V cos (ωt + φ)

B. Start the Waveforms 2015 software. You do not need the AD2 to be plugged in. Using the demo Discovery 2, simulate various waveforms using the wavegen tool. Refer to Appendix C for further details on how to use Waveforms 2015.

Make a comment (1-2 sentences) on what happens to the waveform as you adjust the ampli tude.

Make a comment (1-2 sentences) on what happens to the waveform as you adjust the frequency. Make a comment (1-2 sentences) on what happens to the waveform as you adjust the phase shift.

C. Simulate three signals of varying amplitudes and phase shifts. Maintain the frequency at 30 Hz. D. Express your three signals in both polar and rectangular form.

E. Plot the rectangular form of the equation on the complex plane.

5.2 MultiSim Simulations. Due at the beginning of lab.

A. Simulate the circuit seen in Figure 5.1. Use the following settings for the function generator: • AC Sine Wave • f = 30 Hz • Phase Shift = 50 • Offset = 0 V • Amplitude = 2 V Verify KVL for the circuit by printing out the outputs of each voltmeter and proving KVL.

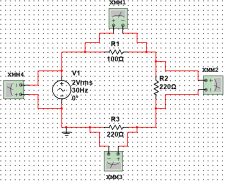
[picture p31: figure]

Figure 5.1: Lab #5 Basic AC KVL Circuit

B. Simulate the circuit seen in Figure 5.2. Use the same function generator settings as 5.2A. Record three to four cycles of both the input and output. Using the cursors on the oscilloscope, measuring the time shift between the maxima of the two waves, ∆t, and use it to calculate the phase shift ∆φ using the following equation:

∆φ = 360 × ∆t × f

C. Using the cursors in the oscilloscope, measure the period T for both the input and output waveforms of Figure 5.2. Use this period to calculate the frequency, f =¹T. Are the frequencies the same for the input and output waveforms?

12

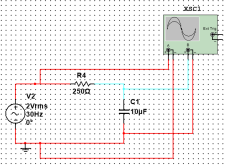
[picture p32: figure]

Figure 5.2: Lab #5 Basic AC RC Circuit

5.3 Laboratory Procedure

0 − 500 Ω

+

Vin

−

10 F

+ −

Vout

Figure 5.3: Lab # 5 Breadboard Connection

A. Connect the potentiometer to an empty portion of the breadboard. Measure and record the minimum and maximum resistance that it can achieve. Refer to Appendix B.2.4 for further details on the potentiometer.

B. Build the circuit in Figure 5.3. Using the waveforms of both Vin and Vout, record what happens to the phase shift, ∆φ, as the resistance of the potentiometer changes.

C. Set the resistance of the potentiometer to its maximum resistance. Measure and record the time shift, ∆t, and use it to calculate the phase shift ∆φ.

D. Save a screenshot of the input and output waveforms when the resistance of the potentiometer is at a maximum. Refer to Appendix C.7.2 on how to appropriately save the screenshot for submission.

E. Measure the RMS voltage of source, potentiometer, and capacitor when the resistance of the potentiometer is at a maximum. Use the AC RMS measurement option of the logger tool.

F. 5.2A has you confirm KVL for Figure 5.1. Does KVL apply for the measurements made in 5.3E? If KVL fails, what information are you missing that should be included?

13

6 Lab # 6: Frequency Response

6.1 PreLab Calculations: Due at the beginning of lab.

A. For the circuit in Figure 6.1, derive the complex valued transfer function, Vout/Vin, in terms of R, L, and the angular frequency ω.

From the transfer function, derive the real valued function for the phase response. Use the variable ω0 for the cutoff frequency, which replaces the ratio R/L.

From the transfer function, derive the real valued function for the magnitude response. Use the variable ω0 for the cutoff frequency, which replaces the ratio R/L.

R

+

+

Vin

−

L

Vout

−

Figure 6.1: Lab # 6 High Pass Filter

B. For the circuit in Figure 6.2, derive the complex valued transfer function, Vout/Vin, in terms of R, L, and the angular frequency ω.

From the transfer function, derive the real valued function for the phase response. Use the variable ω0 for the cutoff frequency, which replaces the ratio R/L.

From the transfer function, derive the real valued function for the magnitude response. Use the variable ω0 for the cutoff frequency, which replaces the ratio R/L.

L

+

+

Vin

−

R

Vout

−

Figure 6.2: Lab # 6 Low Pass Filter

C. Using the magnitude and phase response from 6.1A, determine the inductance L that satisfies the follow conditions, given R = 1 kΩ.

Vin = 10∠0 V Vout = 7.07∠45 V f = 1.3 kHz

D. Using the magnitude and phase response from 6.1B, determine the inductance L that satisfies the follow conditions, given R = 1 kΩ.

Vin = 20∠0 V Vout = 11.2∠ − 56 V f = 4.8 kHz

6.2 MultiSim Simulations: Due at the beginning of lab.

A. Simulate the circuit seen in Figure 6.3a. Use the values for R and L calculated in 6.1C. See Appendix A.5.5 for details on how to use the Bode Plotter.

14

Print out the magnitude and phase plots. See Appendix A.6 on how to properly present results.

What is the magnitude and phase at f = 1.3 kHz? Is that what you expected? Why or why not?

B. Simulate the circuit seen in Figure 6.3b. Use the values for R and L calculated in 6.1D.

Print out the magnitude and phase plots. See Appendix A.6 on how to properly present results.

What is the magnitude and phase at f = 4.8 kHz? Is that what you expected? Why or why not?

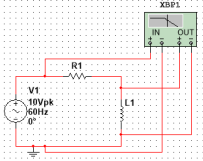
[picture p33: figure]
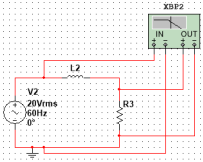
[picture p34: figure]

(a) Lab # 6 High Pass Simulation (b) Lab # 6 Low Pass Simulation

Figure 6.3: fig:Lab # 6 Simulations

6.3 Laboratory Procedure

A. Construct the circuit in Figure 6.4. Set the initial settings of the AC source to be: • AC Sine Wave • f = 1 Hz • Phase Shift = 0 • Offset = 0 V • Amplitude = 2 V

500 Ω

+

+

Vin

−

1 F

Vout

−

Figure 6.4: Lab # 6 Breadboard Connection

B. Measure both the Vin RMS voltage and the Vout RMS voltage. Record these results in Table 5.

C. Repeat the process for all other frequencies in Table 5. Calculate the ratio Vout/Vin for each frequency.

D. Using the data from Table 5, create a Bode Plot of the magnitude response. Remember that the horizontal axis of the plot will be log (f), and the vertical axis will be decibels, which can be calculated through the following equation:

dB = 20 log (Vout/Vin)

15

E. Using your Bode Plot, what is the approximate frequency f when the gain is -3 dB? Record this value, and compare it to the theoretical value calculated using the following equation:

f0 =1

2πRC

F. Is the circuit in Figure 6.4 a high pass or low pass filter? How do you know? Table 5: Lab #6 Measurements

f (Hz) | Vin (mV) | Vout (mV) | Vout/Vin
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
1000
1200

16

7 Lab # 7: Operational Amplifier Integrator and Active Filter 7.1 PreLab Calculations. Due at the beginning of lab.

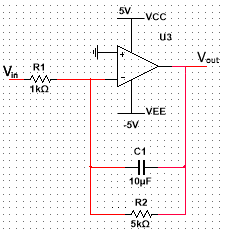
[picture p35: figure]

Figure 7.1: Circuit for Lab # 7

A. Consider the circuit in Figure 7.1 to be an op amp integrator. Using the ideal op amp model and KCL, show that (note: do not consider R2 as part of the circuit):

Vout =−1 R1C

Vin(t)dt

B. If Vin is a square wave, what will the shape of Vout be? Note that you only need to state the shape, and do not need to provide a numeric solution.

C. If Vin is a triangle wave, what will the shape of Vout be? Note that you only need to state the shape, and do not need to provide a numeric solution.

D. If Vin is a sine wave, what will the shape of Vout be? Note that you only need to state the shape, and do not need to provide a numeric solution.

E. Now consider the circuit in Figure 7.1 to be an active low-pass filter. Show that the amplitude response and phase response are:

A(ω) = R2/R1

1 + (ωR2C)²φ(ω) = tan⁻ 1(−ωR2C)

F.

7.2 MultiSim Simulations. Due at the beginning of lab.

A. Simulate the circuit seen in Figure 7.2a. Use the following settings for the function generator: • AC Sine Wave • f = 30 Hz • Phase Shift = 0 • Offset = 0 V • Amplitude = .5 V Note that the circuit acts as a low pass filter. Measure the low frequency gain (dB) and the frequency (Hz) at this gain.

17

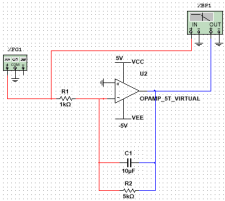
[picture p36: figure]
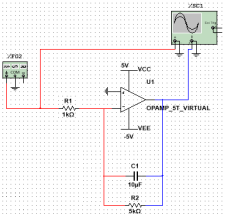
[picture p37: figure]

(a) Lab # 7 Bode Plot Figure (b) Lab #7 AC Plot Figure

Figure 7.2: Lab # 7 Simulation Figures

B. Print out the schematic and the Bode amplitude plot for the circuit in Figure 7.2a.

C. Switch the input waveform type between AC Sine Wave, Square Wave, and Triangle Wave for Figure 7.2b. Print out the associated oscilloscope plots for all three different inputs. Do these match your results in Section 7.1?

7.3 Laboratory Procedures

A. Build the circuit seen in Figure 7.2b. Remember to measure all the component values. Note that the 5 kΩ resistor is constructed using two 10 kΩ resistors.

B. Set the wave generator to the following settings:

• AC Sine Wave • f = 30 Hz • Phase Shift = 0 • Offset = 0 V • Amplitude = .5 V Record the input and output waveforms using the scope tool. Measure the amplitudes of both Vin and Vout, and the phase shift between the waves. Does this match your expected results?

C. Repeat the procedure of 7.3B, except use a square wave instead of a sine wave. D. Repeat the procedure of 7.3B, except use a triangle wave instead of a sine wave.

18

8 Lab # 8: Introduction to Logic Gates

A B C

X Y Z

W

Vout

Figure 8.1: Logic Gate Circuit

8.1 PreLab Calculations: Due at the beginning of lab.

A. Fill out the truth table in Table 6 using Figure 8.1.

B. Looking at the results, what condition for the inputs must hold in order for the output to be 1? (Hint: Look at the number of 1’s versus the number of 0’s that correspond to each output of 1.)

8.2 MultiSim Simulations: Due at the beginning of lab.

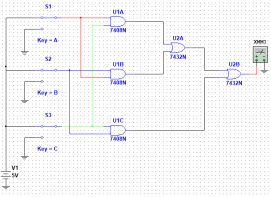
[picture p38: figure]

Figure 8.2: Lab # 8 Simulation

A. Construct the circuit seen in Figure 8.2. Refer to Appendix A for more information on how to use logic gates.

B. Using the circuit you constructed, fill out the truth table seen in Table 7. Note that Vout is the voltage measured by the multimeter.

C. Compare your results for Vout between Tables 6 and 7. Do the results agree with each other? 19

Table 6: Truth Table for Figure 8.1

A B C X Y Z W Vout 0 0 0

0 0 1

0 1 0

0 1 1

1 0 0

1 0 1

1 1 0

1 1 1

8.3 Laboratory Procedure

Table 7: Truth Table for Figure 8.2

A (V) B (V) C (V) Vout (V) 0 0 0

0 0 5

0 5 0

0 5 5

5 0 0

5 0 5

5 5 0

5 5 5

A. Test the inputs and outputs of an AND (7408) gate. Refer to Appendix B for the pin diagram. Don’t forget to supply the chip with 5 V. Fill out the simple truth table seen in Table 8. There are a few important notes to remember when making measurements:

When attempting to get inputs of 1 and 0, you must use either 5 V for 1, or a ground for 0. Leaving an input without anything plugged in will not work.

When making measurements on the output:

– If Vout ≥ 3.5 V, the output may be considered a 1.

– if Vout ≤ 100 mV, the output may be considered a 0.

– If Vout does not fall within these ranges, double check all inputs and outputs are func tioning correctly.

Table 8: Basic 2-Input Truth Table

A B Vout

0 0

0 1

1 0

1 1

B. Test the inputs and outputs of an OR (7432) gate. Refer to Appendix B for the pin diagram. Don’t forget to supply the chip with 5 V. Fill out the simple truth table seen in Table 8.

C. Construct the circuit seen in Figure 8.1. You may use any number of AND and OR chips to build your circuit. Remember to keep track of your inputs and outputs carefully, as to avoid confusion.

D. Using 5 V as an input of 1 and a ground as an input of 0, fill out the truth table seen in Table 7. Confirm these results with both your prelab and your simulations.

20

9 Lab # 9: Introduction to Microcontrollers

9.1 PreLab Calculations. Due at the beginning of lab.

A. Read Appendix D. This appendix contains all the relevant information on the hardware and software associated with microcontrollers.

B. Consider Figure 9.1, which is a simple flowchart representing a blink program. Note that flowcharts are a visual representation of algorithms, which are nothing more than a finite set of precise instructions to solve a problem or to carry out a computation.

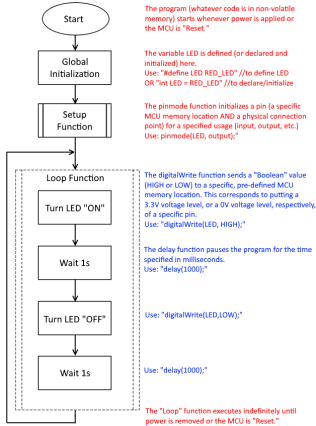
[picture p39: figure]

Figure 9.1: Blink Program Flowchart

C. Modify this flowchart to represent an algorithm which blinks LED1 ON → OFF → ON → OFF, and simultaneously blinks LED2 in the opposite manner, OFF → ON → OFF → ON.

Focus primarily on the loop part of the flowchart.

Details about the other portions of the flowchart will be discussed later in lab. You need only submit the modified flowchart. Additional comments are not necessary.

21

9.2 MultiSim Simulations: Due at the beginning of lab.

There are NO MultiSim simulations for Lab 9.

9.3 Laboratory Procedure

A. Ensure that your LaunchPad and Energia software are running correctly. For detailed instructions on how to set up the devices, see Appendix D.3.1.

B. Run the ”Blink” sketch available in Energia.

This is found in: File → Examples → 01.Basics → Blink

You should also enable line numbers. This is available through: File → Preferences, where you can select ”Display Line Numbers.”

Figure 9.2: Blink Program Sketch

Figure 9.2 shows the code in Energia. Comparing this to Figure 9.1, you’ll see that:

Global Initialization occurs from Line 1 to Line 17.

The ”Setup Function” occurs from Line 19 to Line 23.

The ”Loop Function” occurs from Line 25 to Line 31.

In order to properly run the program, follow the instructions in Appendix D.3.1.

C. Does the Energia sketch do what you expect it to? Discuss whether or not it does, and give a thorough comparison of the flowchart in Figure 9.1 to the code.

D. Modify the ”Blink” sketch to fit the following requirements:

Change the LED from Red to Green.

Change the OFF time to 250 ms, and the ON time to 500 ms.

Run the sketch, and show the working LaunchPad to your TA. Include the modified sketch in your report, either through a screenshot of the code, or the code itself copied and pasted into a word processor.

E. Download and modify the ”Blink2LED student.ino” file to fit the following requirements:

Use an integer counter to track iterations.

For ever iteration, turn LED1 ON for 0.5s, and OFF for 0.5s.

Every fifth iteration, also turn LED2 ON for 0.5s, and OFF for 0.5s.

22

Figure 9.3 shows a flowchart of the modified sketch, with comments that should help you with modifying the code. Show the working LaunchPad to your TA, and include the modified sketch in your report.

F. Download and modify the ”Analog LED student.ino” file to fit the following requirements:

Use an integer counter to track PB1 and PB2 actuation (presses).

For PB1 actuation, increase x if x ¡ 10.

for PB2 actuation, decrease x if x ¿ 0.

Set the LED intensity that is directly proportional to the value of x.

Figure 9.4 shows a flowchart of the modified sketch, with comments that should help you with modifying the code. Show the working LaunchPad to your TA, and include the modified sketch in your report.

G. Download and modify the ”Binary LED student.ino” file to fit the following requirements:

Use an integer count to track the binary state of this 2-bit binary system.

– LED1 represents the Most Significant Bit (MSB)

– LED2 represents the Least Significant Bit (LSB)

Use PB1 to move this binary system from state to state.

Figure 9.5 shows a flowchart of the modified sketch, with comments that should help you with modifying the code. Show the working LaunchPad to your TA, and include the modified sketch in your report.

23

Figure 9.3: Blink2 Program Flowchart

24

Figure 9.4: Analog Program Flowchart

25

Figure 9.5: Binary Program Flowchart

26

Part II

Reference Materials 27

A Appendix A

A.1 Main Window

Figure A.1: Main Window of MultiSim

Looking at Figure A.1, we see the main window of MultiSim that shows up when loading the program. There are three main components that will be focused on, whose descriptions are seen in Table 9. We will explore the different toolbars in subsequent subsections.

Table 9: Descriptions of MultiSim Parts in Figure A.1

Color Label Description

Red Design Window This is where you will place all the

components and measuring devices, and

where a majority of your work will be.

Blue Component Toolbar This is where you will access components and sources that you will put on the design window.

Green Measurement Toolbar This is where you will find measurement tools like multimeters and oscilloscopes.

A.2 Components Toolbar

Figure A.2: Component Toolbar of MultiSim

Figure A.2 is a zoomed in version of the components toolbar, one of the primary toolbars that will be used when doing any simulations. While there is a lot of different options here, there are only a few that you need to keep mind of, which are seen in Table 10.

28

Table 10: Descriptions of Component Toolbar Options

Color Label Description

Red Sources This is where you will access all power

sources and grounds.

Blue Basic Components This is where you will access components

like resistors and capacitors.

Green Analog This is where you will find Operational Amplifiers.

Purple Transistor-Transistor This is where you will find TTL components Logic (TTL) like AND/OR gates.

Pink Simulations This is where you will play, pause

or stop your simulations.

Orange Node Measurements This is where you will access node

voltage and current measurement devices.

A.3 Measurement Toolbar

Figure A.3 is a zoomed in version of the measurement toolbar, the other primary toolbar that will be used during simulations. Here, instead of picking components like resistors and operational amplifiers, you will find primarily measurement tools.

Table 11: Descriptions of Measurement Toolbar Options

Color Label Description

Red Multimeter Primarily used to measure DC current, voltage, and resistance.

Blue Function Generator Not used for measurement. Used to generate AC Signals for AC circuits.

Green Oscilloscope Primarily used to measure AC signals like voltage current.

Purple Bode Plotter Used to generate Bode plots for frequency response.

While there are a variety of measurement tools here, it is not enough to just use the tools and print the results for submission. Instead, you must be conscientious of how to properly present the results. This will be discussed further in the appendix, but is important to note now.

Figure A.3:

Measurement

Toolbar of MultiSim

29

A.4 AC and DC Circuits

A vast majority of circuits you will be using this semester fall into one of two specific categories; alternating current, also known as AC, circuits, or direct current, also known as DC, circuits. We will begin by closely examining power sources and components, and then expanding into how to actually construct circuits.

A.4.1 Power Sources

Looking at Figure A.2, clicking on

the sources button results in a window

popping up, seen in Figure A.5. Un

der the Power Sources tab, the pri

mary three components you need to con

cern yourself with are the DC POWER,

AC POWER, and GROUND compo

nents. Double clicking any of the com

ponents will close the sources window

and return you to the design window.

Figure A.4: AC and DC Power SourcesFigure A.5: Power Sources Window Table 12: Descriptions of Power Source Parts

Color Label Description

Red Name Names each power source. Automatically updates as you place more sources. Blue Value Displays important values associated with the power source Green Nodes Connection points for other components.

From the main window, dou

ble clicking on any source on

the design window will pull up a

second window that allows you

to change any of the parame

ters of the power source. The

windows for DC power sources

and AC power sources are seen

in Figures A.6a and A.6b, re

spectively.

(a) DC Power Source (b) AC Power Source

30

A.4.2 Basic Components

Looking back at Figure A.2, clicking on

the components button results in a win

dow popping up, seen in Figure A.7. The

three primary types of components we will

be focused on are resistors, capacitors,

and inductors, known as passive compo

nents. They are highlighted in Figure A.7.

Figure A.6: Passive Components

Figure A.7: Components Window

Table 13: Descriptions of Passive Component Parts

Color Label Description

Red Name Names each component. Automatically updates as you place more components. Blue Value Displays important values associated with the component. Green Nodes Connection points for other components.

Like the power sources, clicking on any of these components will bring up a window that allows you to change the associated value of the passive component, like the resistance of a resistor. Examples of these windows are seen in Figure A.8

(a) Resistor Window (b) Capacitor Window (c) Inductor Window

Figure A.8: Passive Component Windows

31

A.4.3 Operational Amplifiers

The primary use of the analog tab in

Figure A.2 is to access operational am

plifiers. This results in the window seen

in Figure A.9. From here, there are two

options we are concerned with; virtual

op amps and real op amps. Virtual op

amps can be accessed through the ANA

LOG VIRTUAL tab and results in per

fectly accurate results, where the output

of the op amp obeys theoretical calcula

tions. This differs from real op amps, ac

cessed through the OPAMP tab, whose in

ternal structure will result in minute dif

ferences in output compared to theoretical

results.

Figure A.9: Analog Components Window

Table 14: Operational Amplifiers Terminals

Color Label Description

Red Positive Input Maintains the same sign of the

voltage entering this terminal.

Blue Negative Input Inverts the sign of the voltage

entering this terminal.

Green Positive Voltage Used with the Negative Voltage

Rail Rail to account for offset voltage.

Figure A.10: Virtual Op Amp

Purple Negative Voltage Used with the Positive Voltage. Rail Rail to account for offset voltage.

Pink Output Output of the Op Amp.

Virtual Op Amps are primarily used to compare theoretical values from calculations to simulated values. As such, real op amps in MultiSim will be discussed when examining the integrated circuit and how to use them in the lab.

A.4.4 Digital Logic Components

The TTL tab of Figure A.2 results in

the window seen in Figure A.11. All logic

gates are identified by not by their pur

pose, but by a number. There are also

many duplicate numbers, just with differ

ent letter endings. For the time being, you

may choose to only focus on logic gates

that end with the letter N. Ex: 7400N.

Figure A.11: Analog Components Window

32

Figure A.12: Logic Gates

A.4.5 Basic Circuit Examples

Table 15: Logic Gate Labels

Color Number Purpose Red 7400N NAND Gate Blue 7402N NOR Gate

Green 7404N NOT Gate Purple 7408N AND Gate Pink 7432N OR Gate

(a) DC Circuit (b) AC Circuit

Figure A.13: Basic Circuit Examples

Figures A.13a and A.13b are examples of simple DC and AC circuits, respectively. While there are not many differences between the two, there are still some important features to note:

a) There is a ground, seen by the component beneath the power source. These must be included in all circuits built, and are generally placed at the negative node of a power source.

b) In order to rotate components for easier wire drawing, simply select the component and press CTRL + R.

c) In order to draw wires, simply click on one node of the first component and MultiSim will auto matically draw the wire to the second node you click.

A.5 Making Measurements

Now we must focus on how to make measurements and find the results that are deemed necessary. There are a variety of values you will measure in this lab, and as such, each result requires a different method of measurement.

A.5.1 Multimeter Basics

Multimeters are a unique tool with many different measurement capabilities. However, we will primarily be using them for measuring DC voltages and currents. Multimeters are accessed using the multimeter

33

tab seen in Figure A.3. Clicking on the tab will give you a multimeter to place anywhere on the design window, with a positive and negative terminal to connect to. Double clicking on the multimeter will result in the window seen in Figure A.14.

Table 16: Descriptions of Multimeter Window

Color Label Description

Red Display Displays selected value.

Blue Units Chooses what value

you are measuring.

Green Current Switches between AC

Flow and DC measurements.

Purple Settings Access settings of the multimeter.

Figure A.14: Multimeter Window

A.5.2 Measuring DC Voltage

Using the basic DC circuit example, we will measure the voltage across the resistor R2. In order to accurately measure voltage, there are two criteria to meet:

a) The multimeter must be parallel to the component. This means that one terminal of the multi meter is connected to one node of the component you are measuring across. This is because ideal voltmeters have infinite resistance, and if this is placed in series where current flows through, you will end with inaccurate measurements.

b) The current flowing through the system flows through the positive terminal of the multimeter first, and then the negative terminal. It is important to have this orientation correct in order to ensure the sign of the measurement is accurate. Examples of the two different orientations are seen in Figure A.15.

(a) Correct Orientation (b) Incorrect Orientation

Figure A.15: Orientations for Voltmeter

A.5.3 Measuring DC Current

Again using the basic DC circuit example, we will measure the current flowing through the circuit. In order to accurately measure voltage, there are two criteria to meet:

a) The multimeter must be in series with all other components. This means that the current flows in one terminal of the multimeter and out the other terminal. This is because ideal ammeters have zero resistance, and as such, if placed in parallel, would not read any results.

b) The current flowing through the mutlimeter enters the positive terminal and exists the negative terminal. This is for the same reason as the voltmeter. Examples of the two different cases are seen in Figure A.16

34

(a) Correct Orientation (b) Incorrect Orientation

Figure A.16: Orientations for Ammeter

A.5.4 Using the Oscilloscope

The oscilloscope is the primary tool in MultiSim that will be used for measuring AC signals. We will be using the basic AC circuit as an example and show how to measure different values and manipulate the display. There are a few things to note about the example seen in Figure A.17:

a) There are two channels in the oscil

loscope, channel A and channel B.

This means you may make two dif

ferent measurements at a time.

b) The color of the wires entering the

positive terminal of the channel de

termines the color of the signal on

the oscilloscope.

c) There are some unused ports on the

right of the oscilloscope. These are

known as trigger ports, and will not

be used during your simulations.

Figure A.17: Oscilloscope Attached to Basic AC Circuit

When you click on the oscilloscope after starting a simulation, you will notice that the oscilloscope is outputting hundreds of waveforms a second. This is due to the fact that the oscilloscope is operating in real time. As such, pausing the simulation will also pause the oscilloscope. This will result in the window seen in Figure

Figure A.18: Oscilloscope Window

35

Table 17: Oscilloscope Window Descriptions

Color Label Description

Red Display Displays measured signals.

Blue Cursor Values Displays the current value the cursors are measuring.

Green Timebase Allows you to change the time scale. Increasing the scale will compress the plot, while decreasing the scale expands it.

Purple Channel A Changes the settings of the Channel A signal. The voltage scale refers to the height of the signal. Increasing the scale shrinks the vertical

height of the signal, while decreasing the scale increases the height

of the signal.

Violet Channel B Changes the settings of the Channel B signal. The voltage scale refers to the height of the signal. Increasing the scale shrinks the vertical

height of the signal, while decreasing the scale increases the height

of the signal.

Orange Cursors Allows you to measure specific values at any time in the signal. They are initially on the far left of the display window and can be

dragged anywhere along the signal.

A.5.5 Using the Bode Plotter

Bode Plotters are used when examining

the output of a filter. We will again be

using the basic AC circuit example. The

Bode Plotter is accessed through the Bode

Plotter tab from the measurement toolbar

in Figure A.3. The Bode Plotter has two

channels; an input and an output channel.

Both must be used correctly in order to

create accurate Bode plots. This can be

seen in Figure A.19.

Figure A.19: Bode Plotter Example

Double clicking on the Bode Plotter results in the windows seen in Figure A.20. There are two types of Bode plots; a magnitude plot that displays the gain of the filter in decibels (dB), and a phase plot that displays the phase of the filter in degrees (). You may change the final and initial values of the horizontal and vertical access to zoom in or out of the plots.

(a) Magnitude Bode Plot (b) Phase Bode Plot

Figure A.20: Bode Plotter Results

36

A.5.6 Interpreting TTL Results

TTL is a relatively short topic in this course, and as such, does not need extensive explanation on how to build and understand results in MultiSim. However, it does require some niche components that are not used anywhere else.

Figure A.21: TTL Example

Looking at Figure A.21, there are a few things to note:

a) TTL requires the usage of binary for inputs and outputs. In MultiSim, a 1 corresponds to a 5 V power source, and a 0 corresponds to ground. This means that if 5 V is being sent into a gate, it is receiving a 1 as an input, whereas an input being connected to ground is equivalent to 0.

b) TTL uses switches to flip between 1’s and 0’s. Switches can be found under the Basic components tab, where other passive components are found. There is a ”SWITCH” family, and you will be using the SPDT switch. This can be rotated with CTRL + R, and the key flips the state of the switch. You can change the key at any time by clicking on the switch.

c) Multimeters are used to measure the output of logic gates. The output of the gate goes into the positive terminal of the multimeter, and the negative terminal is connected to ground. Likewise with the input, a 5 V output corresponds to a 1, and a 0 V output corresponds to a 0.

A.6 Presentation of Results

When submitting results, there are some general guidelines to help improve clarity. This is important because results that are clear and easy to read are easier to comprehend for the reader, and will benefit you.

A.6.1 Presenting Numerical Results

Numerical results are relatively easy to present from MultiSim. The quickest method to present results is to open any results windows, like multimeters, and screenshot the main design window using tools like the Snipping Tool in Windows, and COMMAND + SHIFT + 4 in Mac.

A.6.2 Presenting Graphs

Graphs are a more complex result to submit, as by default,the background is black and there is much of the graph interface that does not need to be submitted. As such, there is a separate grapher tool in MultiSim that allows for adjustments. This can be accessed through the grapher button seen in Figure A.22.

37

Figure A.22: Grapher Button in MultiSim

We will be using the basic AC circuit for this example. Clicking on this button results in the window seen in Figure A.23. This is a zoomed out display of what is seen in the oscilloscope. It should be noted that the Grapher should be used when the simulation is either paused or stopped.

Table 18: Descriptions of Graph Window

Color Label Description

Red Cursors Opens up cursors on the display.

Blue Background Changes the background

color between black and white.

Green Square Zoom Allows you to draw a box on

the plot and zoom in on it.

Figure A.23: Grapher Window

An example graph output for submission with cursors should look something like Figure A.24. This format eliminates the black background and zooms in on only four or five waveforms. Cursor values are also easily seen.

Figure A.24: Example Output for Grapher

38

B Appendix B: Breadboard Basics

B.1 How to use the Breadboard

Figure B.1: Breadboard Layout

Figure B.1 shows a small example of a breadboard, one of the main tools you’ll be using throughout the semester. These breadboards are where all of your components will go, and as such, learning to use them is of vital importance. While they may look somewhat intimidating at first, simple guidelines on the breadboard are available in Table 19. Examples of how to use the breadboard are also available in Appendix B.5.

Table 19: Descriptions of Breadboard Parts in Figure B.1

Color Label Description

Red Positive Vertical The red lines on the breadboard indicate a continuous vertical connection along the entire

right side lines. If there are any breaks in the line,

the vertical connection breaks as well.

Blue Negative Vertical The blue lines on the breadboard indicate a continuous vertical connection along the entire

left side lines. If there are any breaks in the line,

the vertical connection breaks as well.

Green Horizontal Connection The 5 holes in a horizontal row indicate a single node. That is, all fives holes inside the green box are connected

to each other, but not connected to anything else.

Purple Vertical Connection The 5 holes in a vertical row indicate a single node. That is, all fives holes inside the purple box are connected

to each other, but not connected to anything else.

39

B.2 Passive Components

In lab, there are many different components you will deal with. The first set of components are called passive components, and consist of resistors, capacitors, and inductors.

B.2.1 Resistors

The first component dealt with also happens to be the most common component you will see, and is called a resistor. Resistors are described by their resistance, which has units of Ohms (Ω). There are a variety of resistors that are available, some examples of which can be seen in Figure B.2.

Figure B.2: Different Resistor Examples

It should be noted that resistors are physically different from each other by the color schemes on the components. These correspond to different numbers, and each combination represents a different resistance value. All possible combinations may be read off of a resistance color code chart, much like the one seen in Figure B.3. Some examples of common resistors are their associated color code are seen in Table 20.

Table 20: Example Resistor Colors

Color Value

Yellow Purple Brown 470 Ω

Brown Black Red 1 kΩ

Red Red Red 2.2 kΩ

Brown Black Orange 10 kΩ

Figure B.3: Resistor Color Code Chart

However, not all resistors are available to you in lab. In the event you need a specific resistance value but do not have a resistor with that exact value, you must utilize the series and parallel properties of resistors. These are described in Table 21.

40

Table 21: Resistor Connections

Image Type Description Horizontal Series Rtot = R1 + R2 Vertical Series Rtot = R1 + R2

Horizontal Parallel ¹

Rtot=¹R1+¹R2

Vertical Parallel ¹

Rtot=¹R1+¹R2

41

B.2.2 Capacitors

The second most common passive component is the capacitor. Capacitors store energy using electric fields, and are defined by their capacitance, which has units of Farads (F). Capacitors are much more easily differentiated from each other, as can be seen in Figure B.4.

Figure B.4: Different Capacitor Examples

Like resistors, putting capacitors in series or parallel will result in components that have different capacitances. However, capacitors in series and parallel obey different rules than resistors. This is seen in Table 22.

Table 22: Capacitor Connections

Image Type Description

Horizontal Series ¹

Ctot=¹C1+¹C2

Vertical Series ¹

Ctot=¹C1+¹C2

Horizontal Parallel Ctot = C1 + C2

Vertical Parallel Ctot = C1 + C2

42

B.2.3 Inductors

The final passive component you will deal with in lab is the inductor. Like capacitors, inductors store energy, but in the form of magnetic fields instead of electric fields. Inductors are identified by their inductance, which has units of Henrys (H).

Figure B.5: Inductor Examples

Inductors take many different forms, but the primary ones you will be using are seen in Figure B.5. Putting inductors in series or parallel results in the same effect as in resistors, and can be seen in Table 23.

Table 23: Inductor Connections

Image Type Description

Horizontal Series Ltot = L1 + L2 Vertical Series Ltot = L1 + L2

Horizontal Parallel ¹

Ltot=¹L1+¹L2

Ltot=¹L1+¹L2

Vertical Parallel ¹

43

B.2.4 Potentiometers

Potentiometers are variable resistors; that is, you may tune potentiometers to have any resistance value ranging from 0 Ω to a set maximum resistance, generally either 500 or 5000 Ω. The two types of poten tiometers you will potentially see are either horizontally or vertically oriented, as seen in Figures B.6a and B.6b, respectively.

(a) Horizontal (b) Vertical (c) Tuner

Figure B.6: Types of Potentiometers and Tools

It should be noted that each potentiometer has three prongs, which differentiates it from the other two terminal components that were previously looked at. Each prong of the potentiometer must go into its own node. In order to tune the potentiometer to a specific resistance, a tuner must be used, as seen in Figure B.6c. This device has a metal tip that fits into the slot of a potentiometer, allowing you to adjust the resistance.

B.3 Operational Amplifiers

Operational Amplifiers, commonly known as Op Amps, are the first of the integrated circuits you will encounter in lab. Op amps are significantly more complex than the two-terminal components, with 8 pins, and require careful attention when using them. It should be noted that each pin of an op amp must have it’s own row on a breadboard. An example of this is seen in Figure B.7. Each pin of the operational amplifier corresponds to a different purpose, which can be seen in the pin diagram in Figure B.8.

Figure B.7: Op Amp on Breadboard Figure B.8: Op Amp Pin Diagram

44

B.4 Logic Gates

Figure B.9: Logic Gate on Breadboard

Logic gates are another integrated circuit you will be using in lab. They are more complex than op amps when wiring, simply due to the number of gates and the amount of pins. Like op amps, each pin must have its own row on the breadboard, as demonstrated in Figure B.9. The different types of logic gates and their corresponding pin layouts are seen in Table 24.

Table 24: Logic Gate Pin Diagrams

Image Number Type Image Number Type

7400 NAND

Gate 7408 AND

Gate

7402 NOR

Gate 7432 OR

Gate

7404 Inverter

B.5 Guidelines for Building Circuits

There are several conventions you may find useful when building circuits. These conventions will help you to maintain a relatively organized breadboard, and streamline the circuit building progress.

Maintain the same shape and component orientation as the circuit diagram. That is, when a component is vertically oriented in a drawing, ensure that the component on the breadboard is also vertically oriented. This should result in you being able to quickly and easily track currents flowing through your circuit. When the circuit is complete, you should be able to look at the circuit from a bird’s eye view and see the same circuit that is in the drawing.

Do not hesitate to use as much of the board as you need. While it may seem simpler at first to use smaller portions of the board to keep everything neat, more often than not you will run into problems trying to fit all the components. There is also an inherent danger in using such little space, as current flowing through tightly coiled wires may overheat.

Use as many colors as you need. Each kit has been equipped with a myriad of wires in various colors and lengths. Each wire is designed to span a specific distance and fits snugly on the board. Using different colors for different connections allows you to easily trace certain connections during

45

debugging. Two general conventions are that the positive voltage source is designated by a red wire, and the grounds are designated by a black wire.

When handling power sources, if you only need one, simply use the rows for the source. If you need more than one power source, such as when using Op Amps, designate one column on the board for positive voltage, and another for ground. This gives you a single location from which all your voltages and grounds span from, since the AD2 only has one positive DC voltage source.

46

C Appendix C: Waveforms 2015 Basics

C.1 Contents of the Analog Discovery 2

The Analog Discovery 2 (AD2) Box contains four main components you need to be concerned with:

(a) AD2 Tool (b) micro-USB to USB Cable

(c) Jumper Wires (d) Pin Connectors

Figure C.1: AD2 Components

a) The actual Analog Discovery tool. It is a clear gray square with the Digilent logo on it. It is seen in Figure C.1a, and is the brain of the system. This will be referred to as the AD2 for the rest of the appendix.

b) A micro-USB to USB cable. This will power the Analog Discovery tool. The micro-USB side attaches to the AD2, while the USB is plugged into the computer that you will be using. This is seen in Figure C.1b.

c) A set of flexible breadboard jumper wires. They are all connected in one bundle, and attached to the bottom of the AD2. Each wire has a specific purpose that is will be explained. These wires are seen in Figure C.1c.

d) A set of pin connectors. These are used to attach the jumper wires to the breadboard, although you may use normal wires as well. The pin connectors are seen in Figure C.1d.

47

C.2 Main Window

Figure C.2: Main Window of Waveforms 2015

The main window of Waveforms 2015 is seen in Figure C.2. There are a lot of options here, but you are only concerned with a few of them for the purpose of this lab.

Table 25: Waveforms 2015 Window Description

Color Label Description

Red Tabs Where you will be able to see tabs of all your tools that are currently in use.

Blue Previous Workspaces Where you can access previous workspaces for other labs easily. Green Scope Tab Used to access the oscilloscope tool. Purple Wave Generator Used to access the wave generator tool.

Pink Voltage Supplies Used to access DC voltage supplies. Orange Voltmeter Used to measure access the voltmeter tool. Teal Logger Used to access the logger tool.

48

C.3 Power Sources

The two primary types of power sources used in this lab are AC and DC voltages. C.3.1 DC Voltage

Figure C.3: DC Voltage Window

In order to generate DC voltages, you must use the Supplies tab on the main window, as seen in Figure C.2. This pulls up the screen seen in Figure C.3, which contains three buttons; a positive supply, a negative supply, and a master enable. You will also notice that a tab appears at the top of the screen, where you may start and stop the tool.

Table 26: DC Voltage Window Description

Color Label Description

Red Master Enable Toggles all voltage sources on and off. Blue Positive Voltage Toggle Toggles the positive voltage source on and off. Green Negative Voltage Toggle Toggles the negative voltage source on and off. Purple Positive Voltage Value Changes the value of the positive voltage source. Pink Negative Voltage Value Changes the value of the negative voltage source.

49

C.3.2 AC Voltage

Figure C.4: AC Voltage Window

In order to generate AC voltages, you must use the Wavegen tab on the main window, as seen in Figure C.2. This pulls up the screen seen in Figure C.4, which has many different options for AC signals. It should be noted you can also use this tool to create DC signals, in the event you need more than the two provided. You will also notice that a tab appears at the top of the screen, where you may start and stop the tool.

Table 27: AC Voltage Window Description

Color Label Description

Red Main Window Space where you will observe the signal shape. You can change the color of the screen by right clicking on it and changing the color.

Blue Wave Type Allows you to switch the wave type between many different choices.

Green Frequency Allows you to change the frequency of the wave, or how often it oscillates in one period.

Purple Amplitude Adjusts the amplitude of the wave, which is the height of both the negative and positive sides of the wave.

Pink Offset Adjusts the vertical offset of the wave, or where the zero of the wave occurs on the y-axis.

Orange Symmetry Adjusts the symmetry of the wave. 50% symmetry means the first half of the wave is the exactly the opposite of the second half,

and vice versa.

Cyan Phase Adjusts the phase of the wave, which is the location of the first zero of the wave.

50

C.4 Making Measurements

The AD2 is capable of measuring both DC and AC values, both of which require different tools. C.4.1 Voltmeter Tool

Figure C.5: Voltmeter Window

The AD2 uses the Voltmeter tool to measure DC and AC voltages, which can be accessed through the tab seen in Figure C.2. Clicking on this tab brings up the Logger window, seen in Figure C.5. You will also notice that a tab appears at the top of the screen, where you may start and stop the tool.

Table 28: Voltmeter Window Description

Color Label Description

Red Channel 1 Values Displays the DC, True RMS, and AC RMS

values measured by Channel 1.

Blue Channel 2 Values Displays the DC, True RMS, and AC RMS

values measured by Channel 2.

51

C.4.2 Logger Tool

Figure C.6: Logger Window

The AD2 uses the Logger tool to measure DC and AC voltages, which can be accessed through the tab seen in Figure C.2. Clicking on this tab brings up the Logger window, seen in Figure C.6. You will also notice that a tab appears at the top of the screen, where you may start and stop the tool.

While this tool performs the same functions as the previously mentioned Voltmeter tool, the Logger tool allows you to observe the evolution of certain values over time. In instances where you need only measure specific values, you may use the Voltmeter tool. If you need to be able to explain how a certain value changes over time, the Logger tool may help to provide more insight.

Table 29: Logger Window Description

Color Label Description

Red Main Window Space where you will see the measured value over time. You can change the color of the screen by right clicking

on it and changing the color.

Blue Channel 1 Values Displays the DC, True RMS, and AC RMS

values associated with Channel 1.

Green Channel 2 Values Displays the DC, True RMS, and AC RMS values associated with Channel 2.

52

C.4.3 Oscilloscope

Figure C.7: Oscilloscope Window

The AD2 has a built in Oscilloscope tool that is used to measure AC values. It is accessed through the Scope tab in Figure C.2. This brings up a window as seen in Figure C.7.

Table 30: Oscilloscope Window Description

Color Label Description

Red Main Window Space where you will observe all signals. You can change the color of the screen by right clicking on it and changing the color.

Blue Time Scale Allows you to change scale of the x-axis and move the screen along the signal. Increasing the scale compresses the plot, while decreasing

the scale expands the signal.

Green Channel 1 Scale Allows you to change the scale of the y-axis and move the screen along the signal for Channel 1. Increasing the scale decreases the height of the

plot, while decreasing the scale increases the height of the plot.

Purple Channel 2 Scale Allows you to change the scale of the y-axis and move the screen along the signal for Channel 2. Increasing the scale decreases the height of the

plot, while decreasing the scale increases the height of the plot.

Pink Cursors Clicking this button will create a cursor that can be dragged along the signal. Clicking the button multiple times will create multiple cursors.

53

C.5 Example Circuit Measurements Figure C.8: Jumper Wire Labels

C.5.1 Example DC Circuit

5 V 1 kΩ

In order to illustrate the use of the AD2, we will use an example and show how mea surements are made in lab. First and fore most is that there are a lot of jumper wires, but you only need a select few. They are labeled in Figure C.8. It should be noted that you do not need to use any of the Digital I/O Signals. Instead focus on the left half of the wire diagram.

(a) Basic DC Circuit Drawing (b) Basic DC Circuit on Breadboard

Figure C.9: Basic DC Circuit

Figure C.9 shows a drawing of a very simple DC

circuit and its equivalent on the breadboard. The

first measurement that must be made is measuring

the voltage of the voltage source; while the voltage

source is supposedly exactly 5 V according to the

Waveforms 2015 software, it may not be supplying

exactly 5 V. Thus, in order to measure the volt

age, we simply measure the supply, in red and black

wires, using parallel green and black wires, as seen

in Figure C.10. Making these measurements through

the Logger tool in Waveforms results in the window

seen in Figure C.11.

Figure C.10: Voltage Source Measurement

54

Figure C.11: Waveforms 2015 Logger Window for Voltage Source

At first glance, the waveform in Figure C.11 looks

very erratic and does not seem stable. However, it is

important to look at the scale on the right side of the

window. From there, we see that the waveform only

oscillates on the scale to 2 mV. Thus the resulting

output of the DC power supply is extremely close to

5 V, but not exactly 5 V. The other measurement

that can be made in this basic example is measuring

the voltage across the resistor. This is done using the

same logger tool as previously used, and an example

circuit with the scopes is seen in Figure C.12. This

results in the window seen in Figure C.13. Figure C.12: Resistor Voltage Measurement

Figure C.13: Waveforms 2015 Logger Window for DC Circuit

55

C.6 Digital Mutlimeter

As powerful as the AD2 is, there are some mea

surements that it is not equipped to make that you

will need for this lab. Instead you will need to

make these measurements using a digital multime

ter (DMM). These devices are not as small as the

AD2, but they are still very practical. The DMM

requires the use of prongs, seen in Figure C.14. The

metal tips of these prongs are placed on the terminals

of whatever component or wire you are measuring.

The DMM itself is seen in Figure C.15, and has a

myriad of functions.

Figure C.14: Digital Multimeter Prongs

Table 31: Descriptions of DMM Options

Color Label Description

Red Ohms Sets the DMM to measure resistance.

Blue Diodes/Capacitors Sets the DMM to measure diode voltage

drop or capacitance.

Green Current Sets the DMM to measure current.

Purple Switcher Switches between white and yellow

options on the dial.

Pink Current Socket The red prong must be plugged in here

if you wish to measure current.

Orange Ground Socket The black prong must always be

plugged in here.

Figure C.15: Digital Multimeter

Cyan Non-Current Socket The red prong must be plugged in here if you wish to measure anything

besides current.

C.6.1 Measuring Resistance

In order to measure the resistance of a resistor,

simply tap the metal leads of the DMM prongs to

either end of a resistor that is isolated from any

power sources or other components. An example of

this can be seen in Figure C.16. Measuring resis

tance is important due to the imperfect nature of

the components you will be using in lab. As an ex

ample, measuring the resistance of the resistor in

Figure C.16 results in a resistance of .944 kΩ, de

spite it being labeled as a 1 kΩ resistor. Figure C.16: Measuring Resistance Example 56

C.6.2 Measuring Capacitance

Likewise with a capacitor, you must measure the

capacitance because despite labels, actual measured

values of capacitance can vary greatly. The same

principle for resistors applies to capacitors; the metal

ends of the prongs touch the terminals of the capac

itor, like in Figure C.17. From this result, we see

that the capacitance is 90.87 F, which is different

from the labeled value of 100 F.

Figure C.17: Measuring Capacitance Example

C.6.3 Measuring Inductance

Unfortunately, the DMM cannot measure inductance. As a result, a secondary device, known as a fluke meter, must be used. The fluke meter can be seen in Figure C.18. While seemingly complex, you only need to use it for one purpose, which can be achieved easily. After the machine is turned on, simply tap the two terminals of the inductor to the black and metal prongs on the bottom right of the fluke meter. The display will then show the inductance.

Figure C.18: Fluke Meter

57

C.6.4 Measuring Current

In order to measure current, you must apply the same principle as when you are measuring current using MultiSim. Using the basic DC circuit example in Figure A, we replace one of the connecting wires with two separate wires, as seen in Figure A. Current must flow through the white wire into the black wire. Thus we complete the circuit using the prongs of the DMM. It should be noted that the circuit is incomplete without using the digital multimeter to measure current; without a connection between the white and black wires, no current can actually flow through the circuit. The resulting accurate current can be seen in Figure C.19b.

(a) DC Current Measurement Circuit (b) Current Reading on DMM

Figure C.19: DC Current Measurement with DMM

C.7 Presentation of Results

Much like in MultiSim, how you present your results is almost as important as what the results are themselves. Clear results make for easier interpretation, and therefore, make it significantly easier for your graders to provide constructive feedback.

C.7.1 Presenting Numerical Results

Numerical results are simple to present. Simply write down or type up the numbers that you read off the screen. While you may screenshot results, in lab it may be more space efficient for your reports to type up the results instead. However, be sure to be very clear about what units you use.

C.7.2 Presenting Graphs

Like MultiSim, Waveforms defaults the background color of the graphs to black. While this improves visibility on the screen, when printing the plots, a black background is both a waste of ink and makes it incredibly difficult to discern specific differences between waveforms in some situations. As a result of this, all plots that are submitted should have a white background.

Figure C.20 shows the default window of Waveforms when measuring a signal using the oscilloscope. When you right click anywhere on the waveform window, a small window will pop up. The most important thing to note is the existence of a ”Color” option. By default, this option is set to dark, and you may switch it to ”Light.” This results in the plot seen in Figure C.21. From here, you may screenshot or snip this waveform, and printing will result in a much easier to read plot.

58

Figure C.20: Oscilloscope with Dark Background

Figure C.21: Oscilloscope with Light Background

59

D Appendix D: Introduction to Microcontrollers D.1 Computers, Processors, and Microcontrollers

A computer is a system (device, machine, etc.) which processes information. Thus, a computer could be an abacus, a computer, or a human. A simplified block diagram of a computer is shown in Figure D.1.

Figure D.1: Simple Block Diagram of a Computer

Modern computers are mainly digital, electronic devices and require many input and output devices (peripherals). An input peripheral might be a keyboard, a touchpad/mouse, a touchscreen, or a mouse. Output peripherals might be monitors or speakers. Any information this computer processes must be in a format which is compatible with that computer. This compatible information is data, typically in the form of digital (binary) and electronic signals.

The actual data processing is mainly carried out by a single Integated Circuit (IC), or ”Microproces sor,” or by a set of microprocessors working together. Note that a microprocessor needs many subsystems working together (different types of memory, different levels of software, and input/output peripherals) to be part of a functional computing system.

A microcontroller is a microprocessor with only basic peripherals and memory. See Figure D.2a for a simple block diagram of a microcontroller. It is much more limited in capability, but has the advantage of being compact in size, with a low power requirement compared to typical, modern computers. A microcontroller, also known as Micro-Controller Unit (MCU), may be embedded into other devices, such as household appliances, automobiles, or robots, to make them more functional. See Figure D.2b for some simple diagrams of MCU’s being embedded in appliances.

(a) Block Diagram (b) Typical Applications

Figure D.2: Microcontroller Diagrams

Since MCU’s have very limited hardware compared to typical computers, they also have much more limited software capabilities. This is an advantage for MCU’s, since embedded MCU’s do not need a lot of space for keyboards or monitors, and do not need advanced operating systems or software. MCU’s are designed to run as standalone programmable computing systems. On the other hand, the limited hardware and software can be disadvantageous, as MCU”s are not user-friendly and capable as compared to typical computers.

A typical microcontroller does not have, or even need, its own operating system, and does not have a ”Run” command. A typical microcontroller simply executes whatever program it has in its program space (of non-volatile memory) which is typically of the structure shown in Figure D.3. The ”Global Initialization” block contains the declaration and initialization of global variables, and includes any special hardware libraries needed (for particular sensors or actuators). The ”Setup Function” block initializes any of the hardware resources needed. Note that the ”Global Initialization” and ”Setup Function”

60

block both execute only once, generally when the microcontroller is powered on or reset. The ”Loop Function” block contains the ”meat” of the microcontroller’s program, repeating indefinitely until the microcontroller is powered down or reset.

Figure D.3: Generic MCU Program Flowchart

D.2 MSP432 LaunchPad - Hardware Overview

This lab uses a specific MCU platform, known as the MSP432 LaunchPad, which is manufactured by Texas Instruments. A photograph of this device is show in Figure D.4. You may visit http:// energia.nu/pin-maps/guide_msp432p401r/ or http://www.ti.com/tool/MSP-EXP432P401R for more information.

Figure D.4: MSP432 LaunchPad Hardware Layout

61

When looking at Figure D.4, there are a few things to consider:

Orientation and Handling

– Orient the LaunchPad as shown in Figure D.4. That is, ensure that the Texas Instrument Logo is at the top of the board, and the majority of the white labels were right side up.

– Keep the LaunchPad on a level surface, away from conductive materials and fluids. – When holding the LaunchPad, hold it by the edges.

USB Port

– Power and communication is provided by a USB cable connecting a host computer USB port to this micro-USB port on the LaunchPad.

– This micro-USB port is delicate, so handle it carefully.

– If you need to temporarily remove power from the LaunchPad, disconnect the other end of the USB cable.

RESET

– User reset is provided by a pushbutton switch actuated from the top side of the LaunchPad. – Use this switch if you need to ”reboot” the LaunchPad.

User-Output is provided by means of LED1 (a single red LED) and LED2 (a three-color, RGB LED). These devices are useful indicators of a program while it is running.

User-Input is provided by means of PUSH1 (a pushbutton switch, actuated from the Left side of the LaunchPad) and PUSH2 (a pushbutton switch, actuated from the Rights ide of the LaunchPad). These devices are to prompt a program to change execution while it is running.

The GPIO (General-Purpose Input/Output) pins of a microcontroller provide the user access to connecting other devices to it. These are discussed in Section D.2.1.

D.2.1 MSP432 LaunchPad Pin Map

A pin map is a table of MCU pins, their physical locations, their hardware names (also known as schematic labels), their software names (also known as software addresses), and their available functions. The microcontroller’s pins provide the means for users to connect physical devices to the microcontroller. Thus, a pin map is truly the ”map” for connecting the MCU hardware and software to physical appli cations. A pin map for the MSP432 LaunchPad can be seen in Figure D.5, but is also availble online at http://energia.nu/pin-maps/guide_msp432p401r/.

Note that the physical locations of the MSP432 LaunchPad pins are listed in white-on-black text, while the hardware names are color coded depending on the pin’s programmable functions. As an example, pin P6 0, located at J1,2, is shaded green because it is only capable of using the ”Digital Read” and ”Digital Write” functions, whereas P3 2, located right below at J1,3, is shaded purple because it is capable of ”Analog Write” along with ”Digital Read” and ”Digital Write” functions.

ins with specific hardware names are listed in white-on-gray text, in addition to being color-coded by pin label. For example, P1 1 is also listed as PUSH1 because it is connected to the Left pushbutton switch as previously described. While a pin map may seem overwhelming at first, it is essential to connecting a microcontroller to various applications using physical devices and as you use the device more, you will be more familiar with it.

D.3 Energia - Software Overview

This lab uses Energia to program the MSP432 LaunchPad. Energia is one of many forms of Embedded C, which is a C-language platform with additional libraries that enables the microcontroller to interface directly with physical devices such as sensors, actuators, or other microcontrollers. ”Arduino” is another popular version of Embedded-C which runs many Arduino MCU’s.

62

Figure D.5: MSP432 LaunchPad Pin Map

The interface of Energia’s programming environment is seen in Figure D.6. Much more information, including video tutorials and documentation is available both online at http://energia.nu/, and in the installation folder, under the ”references” sub-folder.

Figure D.6: Energia Interface Window

63

When considering Figure D.6:

Menu Bar

– Most Energia functions may be accessed through this interface.

– The Help menu provides a quick connection to a Reference of all Energia commands. – The Tools menu provides a way to check and change the COM port.

Short-cut Icons

– The Verify and Upload icons are extremely important to compiling and uploading code from Energia’s host programming environment to the LaunchPad.

There is no ”Run” command or icon. Once a sketch is uploaded to the LaunchPad, the LaunchPad executes this code automatically.

There is no ”Stop” command or icon. The LaunchPad executes whatever program it has in its program memory until it is reset or if power is disconnected.

– The Serial Monitor provides a means for the user to see data output from the program while the program is running. This is very helpful for verifying the program’s execution, especially when the program does not execute its instructions as expected.

Energia Sketch (coding window)

– This is where a user inputs or modifies Energia commands.

– Note that Energia saves the sketch in a folder of the same name as the sketch each time a sketch is compiled.

Status Bar: This is where Energia’s operations are reported.

Message Window: This is where Warnings and Error Messages are reported. HW Settings: This is a summary of the Energia/LaunchPad setup.

D.3.1 Running an Energia Sketch

Before compiling any code, you must ensure that Energia is set up properly with correct settings. On the Energia main window, verify the following settings:

– Tools → Boards: ”RED LaunchPad w/ msp432 EMT (48MHz)” should appear. – Tools → Port: should appear to be grayed-out when the LaunchPad is not connected.

Connect the LaunchPad to the PC.

– Use the USB(male) to microUSB(male) cable that is provided.

– When connecting the LaunchPad, be sure to handle the ports carefully.

– When successfully connected, a green LED on the left side of the LaunchPad should be on. Verify the COM port:

– Tools → Port: ”COMx” should now appear, now that the LaunchPad is connected.

– ”COMx” will be different for different combinations of PC and LaunchPad (COM4, COM5, etc.)

– Generally, two COM ports should appear available as serial ports.

However, only one serial port is used by Energia at any given time.

Select the highest-numbered COM port that is available.

If you can’t see data in the Serial monitor, try switching COM ports.

64

After confirming all your settings are correct, open an Energia program (they are called sketches in the software). There are many examples available directly through Energia or various forums online. For this course, it is usually best to start with a program which has already been developed that is similar to your requirements, and modify it to meet your particular needs. From there, you must both verify and upload the sketch that you want to run. The buttons are seen in Figure D.7.

Figure D.7: Verify and Upload Buttons

Verifying the code will display many compiler messages in the status window, which is seen in Fig ure D.8.

While these messages will be in red text, there is no cause for concern. This is normal, even for working code.

Watch the status bar in the top right of Figure D.8. When the verification is done, you should see a ”Done Compiling” message on the status bar. This indicates that the program was compiled without errors.

Figure D.8: Status Window

After verifying that the code compiles successfully, you will upload the program to the LaunchPad.

Again, you will see many compiler messages in red displayed in the status window. Like before, this is normal, but you may note that there are some errors when reading the messages.

When you again see the ”Done Uploading” status, you should see the ”Success” message pop up in the status window, like in Figure D.9. This indicates that the program is running successfully, and should be seen on your LaunchPad.

Figure D.9: Complete Status

65

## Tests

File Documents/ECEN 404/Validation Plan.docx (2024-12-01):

Test | FSR Paragraph # | Owner | Status | Success Criterion | Methodology
Buck Converter 12 -> 5 V | 3.2.3.3.1 | RF | Succesful | Intakes 12 V DC outputs 5 V DC | Measured with multimeter
Buck Converter 5 -> 3 V | 3.2.3.3.1 | RF | Succesful | Intakes 12 V DC outputs 3 V DC | Measured with multimeter
Buck Converter 5 -> -5 V | 3.2.3.3.1 | RF | Succesful | Intakes 5 V DC outputs -5 V DC | Measured with multimeter
Wave Gen Powers On | 3.2.3.1.5 | YH | Succesful | Outputs voltage when provided 5 V supply power | Measured with multimeter
Wave Gen Amplitude | 3.2.3.1.5 | YH | Succesful | Outputs 0.5, 1, and 2 V successfully | Measured with multimeter
Wave Gen Frequency | 3.2.1.3 | YH | Succesful | Outputs frequencies 1, 20, and 30 Hz | Measured with oscilloscope
Wave Gen Output Shape | 3.2.1.3 | YH | Succesful | Produces sine, square, and triangular waves at all 3 amplitudes and frequencies | Measured with oscilloscope
Wave Gen Noise | 3.2.3.2.1 | YH | Succesful | Output signal is moderately accurate | Measured with oscilloscope
Ammeter | 3.2.1.4 | PZ | Succesful | Able to read 0.5 A of current | Measured with multimeter
Ohmmeter | 3.2.1.4 | PZ | Succesful | Able to read 100 ohms and 10k ohms | Measured with multimeter
Duty Cycle | 3.2.3.1.5 | YH | Succesful | Can produce a square wave with 50% duty cycle | Measured with oscilloscope
App Connects to Bluetooth | 3.2.1.1 | LDS | Succesful | App connects to ESP32 | Observation from app and code terminal
App Receives/Sends Data from/to ESP32 | 3.2.1.1 | LDS | Succesful | ESP32 reacts to commands sent from the app / App displays message from ESP32 | Observation from app and code terminal
App - Multimeter Function | 3.2.3.1.3 | LDS + PZ | Succesful | App displays correct parameter with correct value | Observation from app and code terminal
App - Oscilloscope Function | 3.2.3.1.3 | LDS + PZ | Succesful | App displays accurate graph and can display requested parameters | Compare to actual oscilloscope
App - Waveform Gen Function | 3.2.3.1.3 | LDS + YH | Succesful | App takes in appropriate settings and communicates with ESP32 to output correct signal | Observation from app, code terminal, and oscilloscope
App - Power Supply Function | 3.2.3.1.3 | LDS + RF | Succesful | App triggers Lab Kit to output power | Measured with multimeter and observed from app
Switching Menus Within App | 3.2.1.1 | LDS | Succesful | Can switch to a different menu within app while not disabling previous action | Observation from app and ESP32
App Works on IOS | 3.2.1.1 | LDS | Succesful | App is downloaded and operates with all functionality | Observation from phone
App Works on Android | 3.2.1.1 | LDS | Succesful | App is downloaded and operates with all functionality | Observation from phone
ADC Power | 3.2.1.2 | PZ | Succesful | ADC powers on and interprets analog signal into binary output correctly | Observation from
ADC Speed | 3.2.1.2 | PZ | Succesful | ADC reads voltages fast enough to produce a smooth sine wave of at least 60 Hz | Observed through use of application and real oscilloscope
ADC Amplitude | 3.2.1.2 | PZ | Succesful | ADC can read between 0, 2.5 and 5 V | Observation from app and code terminal
ESP32 Power | 3.2.3.1.1 | RF | Succesful | Turns on with correct input signals | Observation code terminal
ESP32 Communicates With App | 3.2.1.1 | Team | Succesful | ESP32 communicates via Bluetooth and sends/receives data from the app | Observation from app and code terminal
ESP32 Communicates With Wave Gen | 3.2.3.1.5 | Team | Succesful | ESP32 sends correct information to waveform generator | Observation from app, code terminal, and oscilloscope
ADC Communicates With ESP32 | 3.2.1.2 | Team | Succesful | ESP32 correctly reads digital input from ADC | Observation from code terminal
ESP32 Communicates With Power Supply | 3.2.1.5 | Team | Succesful | ESP32 triggers circuit to output power | Observation from multimeter and terminal
Kit runs at max current/voltage for 30 minutes | 3.2.4 | Team | Succesful | Kit can run at max outputs for extended period of time without catastrophic device failure or inappropriately excess noise | Validated by validating everything else

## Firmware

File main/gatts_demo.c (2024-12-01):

/*
 * SPDX-FileCopyrightText: 2021-2024 Espressif Systems (Shanghai) CO LTD
 *
 * SPDX-License-Identifier: Unlicense OR CC0-1.0
 */

/****************************************************************************
 *
 * This demo showcases BLE GATT server. It can send adv data, be connected by client.
 * Run the gatt_client demo, the client demo will automatically connect to the gatt_server demo.
 * Client demo will enable gatt_server's notify after connection. The two devices will then exchange
 * data.
 *
 ****************************************************************************/

#include <stdio.h>
#include <stdlib.h>
#include <string.h>
#include <inttypes.h>
#include "freertos/FreeRTOS.h"
#include "freertos/task.h"
#include "freertos/event_groups.h"
#include "esp_system.h"
#include "esp_log.h"
#include "nvs_flash.h"
#include "esp_bt.h"
#include "driver/spi_master.h"
#include "driver/gpio.h"
#include "esp_rom_gpio.h" // Direct GPIO access
#include "soc/rtc_periph.h"

#include "esp_gap_ble_api.h"
#include "esp_gatts_api.h"
#include "esp_bt_defs.h"
#include "esp_bt_main.h"
#include "esp_bt_device.h"
#include "esp_gatt_common_api.h"

#include "sdkconfig.h"

#include "esp_timer.h"

#define GATTS_TAG "ECEN 215 Lab Kit"

/// Declare the static function
static void gatts_profile_a_event_handler(esp_gatts_cb_event_t event, esp_gatt_if_t gatts_if, esp_ble_gatts_cb_param_t *param);

#define GATTS_SERVICE_UUID_TEST_A 0x00FF
#define GATTS_CHAR_UUID_TEST_A 0xFF01
#define GATTS_DESCR_UUID_TEST_A 0x3333
#define GATTS_NUM_HANDLE_TEST_A 4

static bool oscilloscope_mode = false;
static bool voltmeter_mode = false;
static bool ammeter_mode = false;
static bool ohmmeter_mode = false;

#define TEST_DEVICE_NAME "ECEN 215 Lab Kit"
#define TEST_MANUFACTURER_DATA_LEN 17

#define GATTS_DEMO_CHAR_VAL_LEN_MAX 0x40

#define PREPARE_BUF_MAX_SIZE 1024

static uint8_t char1_str[] = {0x11, 0x22, 0x33};
static esp_gatt_char_prop_t a_property = 0;

static esp_attr_value_t gatts_demo_char1_val =
    {
        .attr_max_len = GATTS_DEMO_CHAR_VAL_LEN_MAX,
        .attr_len = sizeof(char1_str),
        .attr_value = char1_str,
};

static uint8_t adv_config_done = 0;
#define adv_config_flag (1 << 0)
#define scan_rsp_config_flag (1 << 1)

#ifdef CONFIG_SET_RAW_ADV_DATA
static uint8_t raw_adv_data[] = {
    0x02, 0x01, 0x06,       // Length 2, Data Type 1 (Flags), Data 1 (LE General Discoverable Mode, BR/EDR Not Supported)
    0x02, 0x0a, 0xeb,       // Length 2, Data Type 10 (TX power level), Data 2 (-21)
    0x03, 0x03, 0xab, 0xcd, // Length 3, Data Type 3 (Complete 16-bit Service UUIDs), Data 3 (UUID)
};
static uint8_t raw_scan_rsp_data[] = { // Length 15, Data Type 9 (Complete Local Name), Data 1 (ESP_GATTS_DEMO)
    0x0f, 0x09, 0x45, 0x53, 0x50, 0x5f, 0x47, 0x41, 0x54, 0x54, 0x53, 0x5f, 0x44,
    0x45, 0x4d, 0x4f};
#else

static uint8_t adv_service_uuid128[32] = {
    /* LSB <--------------------------------------------------------------------------------> MSB */
    // first uuid, 16bit, [12],[13] is the value
    0xfb,
    0x34,
    0x9b,
    0x5f,
    0x80,
    0x00,
    0x00,
    0x80,
    0x00,
    0x10,
    0x00,
    0x00,
    0xEE,
    0x00,
    0x00,
    0x00,
    // second uuid, 32bit, [12], [13], [14], [15] is the value
    0xfb,
    0x34,
    0x9b,
    0x5f,
    0x80,
    0x00,
    0x00,
    0x80,
    0x00,
    0x10,
    0x00,
    0x00,
    0xFF,
    0x00,
    0x00,
    0x00,
};

// The length of adv data must be less than 31 bytes
// static uint8_t test_manufacturer[TEST_MANUFACTURER_DATA_LEN] =  {0x12, 0x23, 0x45, 0x56};
// adv data
static esp_ble_adv_data_t adv_data = {
    .set_scan_rsp = false,
    .include_name = true,
    .include_txpower = false,
    .min_interval = 0x0006, // slave connection min interval, Time = min_interval * 1.25 msec
    .max_interval = 0x0010, // slave connection max interval, Time = max_interval * 1.25 msec
    .appearance = 0x00,
    .manufacturer_len = 0,       // TEST_MANUFACTURER_DATA_LEN,
    .p_manufacturer_data = NULL, //&test_manufacturer[0],
    .service_data_len = 0,
    .p_service_data = NULL,
    .service_uuid_len = sizeof(adv_service_uuid128),
    .p_service_uuid = adv_service_uuid128,
    .flag = (ESP_BLE_ADV_FLAG_GEN_DISC | ESP_BLE_ADV_FLAG_BREDR_NOT_SPT),
};
// scan response data
static esp_ble_adv_data_t scan_rsp_data = {
    .set_scan_rsp = true,
    .include_name = true,
    .include_txpower = true,
    //.min_interval = 0x0006,
    //.max_interval = 0x0010,
    .appearance = 0x00,
    .manufacturer_len = 0,       // TEST_MANUFACTURER_DATA_LEN,
    .p_manufacturer_data = NULL, //&test_manufacturer[0],
    .service_data_len = 0,
    .p_service_data = NULL,
    .service_uuid_len = sizeof(adv_service_uuid128),
    .p_service_uuid = adv_service_uuid128,
    .flag = (ESP_BLE_ADV_FLAG_GEN_DISC | ESP_BLE_ADV_FLAG_BREDR_NOT_SPT),
};

#endif /* CONFIG_SET_RAW_ADV_DATA */

static esp_ble_adv_params_t adv_params = {
    .adv_int_min = 0x20,
    .adv_int_max = 0x40,
    .adv_type = ADV_TYPE_IND,
    .own_addr_type = BLE_ADDR_TYPE_PUBLIC,
    //.peer_addr            =
    //.peer_addr_type       =
    .channel_map = ADV_CHNL_ALL,
    .adv_filter_policy = ADV_FILTER_ALLOW_SCAN_ANY_CON_ANY,
};

#define PROFILE_NUM 2
#define PROFILE_A_APP_ID 0
#define PROFILE_B_APP_ID 1

int timer_0_cnt = 0;
int timer_1_cnt = 0;

struct gatts_profile_inst
{
    esp_gatts_cb_t gatts_cb;
    uint16_t gatts_if;
    uint16_t app_id;
    uint16_t conn_id;
    uint16_t service_handle;
    esp_gatt_srvc_id_t service_id;
    uint16_t char_handle;
    esp_bt_uuid_t char_uuid;
    esp_gatt_perm_t perm;
    esp_gatt_char_prop_t property;
    uint16_t descr_handle;
    esp_bt_uuid_t descr_uuid;
};

/* One gatt-based profile one app_id and one gatts_if, this array will store the gatts_if returned by ESP_GATTS_REG_EVT */
static struct gatts_profile_inst gl_profile_tab[PROFILE_NUM] = {
    [PROFILE_A_APP_ID] = {
        .gatts_cb = gatts_profile_a_event_handler,
        .gatts_if = ESP_GATT_IF_NONE, /* Not get the gatt_if, so initial is ESP_GATT_IF_NONE */
    },
};

typedef struct
{
    uint8_t *prepare_buf;
    int prepare_len;
} prepare_type_env_t;

static prepare_type_env_t a_prepare_write_env;

void example_write_event_env(esp_gatt_if_t gatts_if, prepare_type_env_t *prepare_write_env, esp_ble_gatts_cb_param_t *param);
void example_exec_write_event_env(prepare_type_env_t *prepare_write_env, esp_ble_gatts_cb_param_t *param);

static void gap_event_handler(esp_gap_ble_cb_event_t event, esp_ble_gap_cb_param_t *param)
{
    switch (event)
    {
#ifdef CONFIG_SET_RAW_ADV_DATA
    case ESP_GAP_BLE_ADV_DATA_RAW_SET_COMPLETE_EVT:
        adv_config_done &= (~adv_config_flag);
        if (adv_config_done == 0)
        {
            esp_ble_gap_start_advertising(&adv_params);
        }
        break;
    case ESP_GAP_BLE_SCAN_RSP_DATA_RAW_SET_COMPLETE_EVT:
        adv_config_done &= (~scan_rsp_config_flag);
        if (adv_config_done == 0)
        {
            esp_ble_gap_start_advertising(&adv_params);
        }
        break;
#else
    case ESP_GAP_BLE_ADV_DATA_SET_COMPLETE_EVT:
        adv_config_done &= (~adv_config_flag);
        if (adv_config_done == 0)
        {
            esp_ble_gap_start_advertising(&adv_params);
        }
        break;
    case ESP_GAP_BLE_SCAN_RSP_DATA_SET_COMPLETE_EVT:
        adv_config_done &= (~scan_rsp_config_flag);
        if (adv_config_done == 0)
        {
            esp_ble_gap_start_advertising(&adv_params);
        }
        break;
#endif
    case ESP_GAP_BLE_ADV_START_COMPLETE_EVT:
        // advertising start complete event to indicate advertising start successfully or failed
        if (param->adv_start_cmpl.status != ESP_BT_STATUS_SUCCESS)
        {
            ESP_LOGE(GATTS_TAG, "Advertising start failed");
        }
        break;
    case ESP_GAP_BLE_ADV_STOP_COMPLETE_EVT:
        if (param->adv_stop_cmpl.status != ESP_BT_STATUS_SUCCESS)
        {
            ESP_LOGE(GATTS_TAG, "Advertising stop failed");
        }
        else
        {
            ESP_LOGI(GATTS_TAG, "Stop adv successfully");
        }
        break;
    case ESP_GAP_BLE_UPDATE_CONN_PARAMS_EVT:
        ESP_LOGI(GATTS_TAG, "update connection params status = %d, min_int = %d, max_int = %d,conn_int = %d,latency = %d, timeout = %d",
                 param->update_conn_params.status,
                 param->update_conn_params.min_int,
                 param->update_conn_params.max_int,
                 param->update_conn_params.conn_int,
                 param->update_conn_params.latency,
                 param->update_conn_params.timeout);
        break;
    case ESP_GAP_BLE_SET_PKT_LENGTH_COMPLETE_EVT:
        ESP_LOGI(GATTS_TAG, "packet length updated: rx = %d, tx = %d, status = %d",
                 param->pkt_data_length_cmpl.params.rx_len,
                 param->pkt_data_length_cmpl.params.tx_len,
                 param->pkt_data_length_cmpl.status);
        break;
    default:
        break;
    }
}

void example_write_event_env(esp_gatt_if_t gatts_if, prepare_type_env_t *prepare_write_env, esp_ble_gatts_cb_param_t *param)
{
    esp_gatt_status_t status = ESP_GATT_OK;
    if (param->write.need_rsp)
    {
        if (param->write.is_prep)
        {
            if (param->write.offset > PREPARE_BUF_MAX_SIZE)
            {
                status = ESP_GATT_INVALID_OFFSET;
            }
            else if ((param->write.offset + param->write.len) > PREPARE_BUF_MAX_SIZE)
            {
                status = ESP_GATT_INVALID_ATTR_LEN;
            }
            if (status == ESP_GATT_OK && prepare_write_env->prepare_buf == NULL)
            {
                prepare_write_env->prepare_buf = (uint8_t *)malloc(PREPARE_BUF_MAX_SIZE * sizeof(uint8_t));
                prepare_write_env->prepare_len = 0;
                if (prepare_write_env->prepare_buf == NULL)
                {
                    ESP_LOGE(GATTS_TAG, "Gatt_server prep no mem");
                    status = ESP_GATT_NO_RESOURCES;
                }
            }

            esp_gatt_rsp_t *gatt_rsp = (esp_gatt_rsp_t *)malloc(sizeof(esp_gatt_rsp_t));
            if (gatt_rsp)
            {
                gatt_rsp->attr_value.len = param->write.len;
                gatt_rsp->attr_value.handle = param->write.handle;
                gatt_rsp->attr_value.offset = param->write.offset;
                gatt_rsp->attr_value.auth_req = ESP_GATT_AUTH_REQ_NONE;
                memcpy(gatt_rsp->attr_value.value, param->write.value, param->write.len);
                esp_err_t response_err = esp_ble_gatts_send_response(gatts_if, param->write.conn_id, param->write.trans_id, status, gatt_rsp);
                if (response_err != ESP_OK)
                {
                    ESP_LOGE(GATTS_TAG, "Send response error\n");
                }
                free(gatt_rsp);
            }
            else
            {
                ESP_LOGE(GATTS_TAG, "malloc failed, no resource to send response error\n");
                status = ESP_GATT_NO_RESOURCES;
            }
            if (status != ESP_GATT_OK)
            {
                return;
            }
            memcpy(prepare_write_env->prepare_buf + param->write.offset,
                   param->write.value,
                   param->write.len);
            prepare_write_env->prepare_len += param->write.len;
        }
        else
        {
            esp_ble_gatts_send_response(gatts_if, param->write.conn_id, param->write.trans_id, status, NULL);
        }
    }
}
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

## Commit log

2024-12-01 Adding all presentations, documents, etc. from ECEN 403/404.
    [Calculate_Freq_Input_For_AD9833.xlsx, Captone Gantt Chart.xlsx, Currently Owned List of Parts 10_3_24.xlsx, Execution Plan.xlsx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]
2024-12-02 Adding PCB and Case files
    [Copy of -5V Buck and Power Jack.SchDoc, Copy of 3.3V Buck.SchDoc, Copy of 5 and -5 Supply Switches.SchDoc, Copy of 5V Buck.SchDoc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]
2024-12-02 Update README.md
    Added color coding and label for wires.
2024-12-02 Update README.md
    Testing formatting of wires
